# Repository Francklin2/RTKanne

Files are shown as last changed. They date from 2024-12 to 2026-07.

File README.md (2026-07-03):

# RTKanne
A Bluetooth RTK rover on a stick or box for blind people (Un rover RTK Bluetooth pour aveugles en boitier ou a fixer sur une canne)
English version below

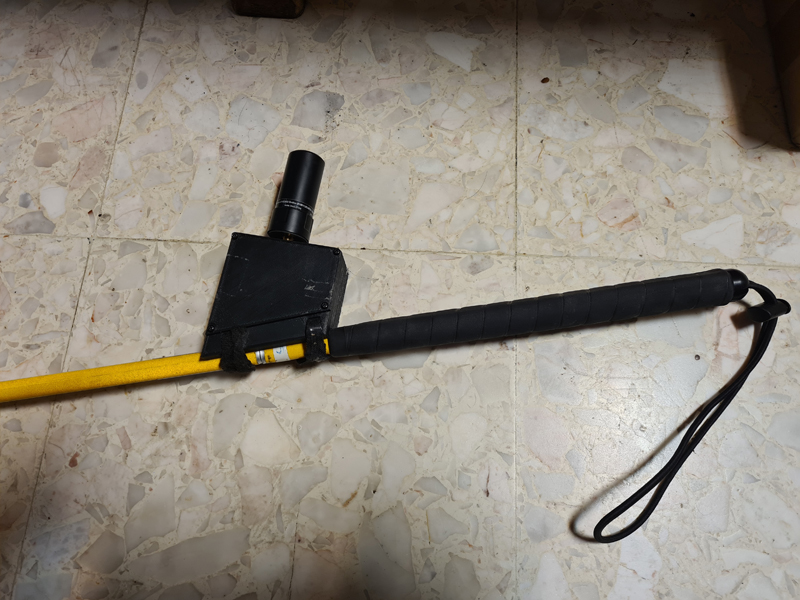
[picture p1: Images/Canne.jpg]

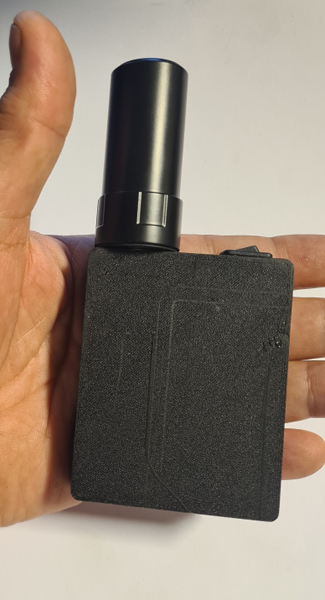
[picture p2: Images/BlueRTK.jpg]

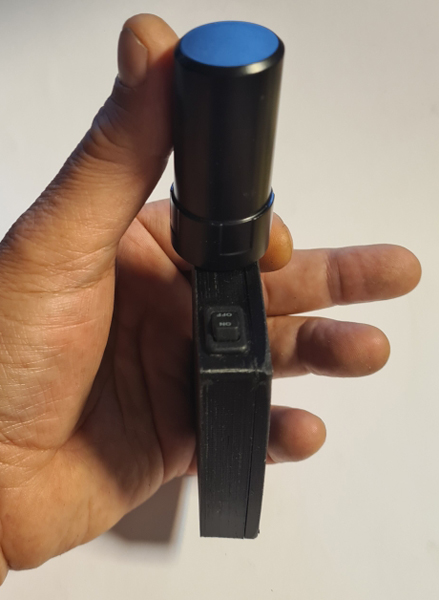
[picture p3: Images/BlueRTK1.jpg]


Les projets RTKanne et Blue RTK sont des rover RTK pour aveugles et malvoyants qui peuvent se fixer sur une canne (projet initial RTKanne) ou un boitier plus compact à mettre dans une pochette sur la poitrine avec le smartphone ou même dans une poche de ses vêtement (projet final Blue RTK),il peut fournir une précision de quelques centimètres a une application IOS ou Android. Le système est composé du ZED-X20P, un module bluetooth  ou un Bluetooth Xiao ESP32C3 (Ardusimple sur RTKANNE), une batterie interne avec son chargeur BMS USB-C et un régulateur 3,3 Volts Pololu. Un PCB de carte mère et un nouveau boitier on été développé par My Human Kit à Rennes afin de fiabiliser le boitier et simplifier sa fabrication (My Human Kit est un Fablab dédié au handicap).

Ce récepteur utilise le réseau NTRIP du réseau open source Centipede (centipede.fr) fonctionnant en France et dans certains pays d'Europe pour obtenir les corrections RTK (une connexion a internet via le smartphone est requise). 
La précision de position RTK ne permet de résoudre qu'une partie du problème de navigation et de guidage d'un aveugle, si on a bien une position précise, il faut en plus un logiciel de navigation qui soit adapté a ce niveau de précision, par exemple Google maps piéton valide un point de navigation alors que l'on est dans un rayon d'une dizaine de mètres de ce point, cette imprécision dans la carte de navigation et du trajet ne permet pas le guidage correct d'un aveugle même en RTK, il faut donc que le logiciel et le trajet de navigation soient adaptés pour tirer pleinement profit d'un positionnement précis. Pour l'instant seule l'application Sonarvision sur IOS propose des trajets précis au mètre prés  pour les aveugles et malvoyant grâce au VPS (visual positionning system) ou au récepteur RTK 

    Utilisation sur IOS
   L'application Sonarvision est disponible avec l'option RTK depuis mi 2025 avec de nouvelles fonctionnalités  afin de profiter pleinement des possibilités du RTK comme l'enregistrement de traces pour créer un parcours hors zone couvertes par le VPS ou sans passer par l'éditeur de trajets, l'application est disponible sur sonarvision.fr ou sur l'appstore. Pour tester le bon fonctionnement du Rover RTKanne, vous pouvez aussi utiliser SWmaps disponible sur l'apple store ou installer le code de Client Ntrip présent sur ce dépôt a l'aide de Xcode, il faut installer Xcode sur un Mac, charger et compiler le code de Client Ntrip, connecter l'iPhone en mode développeur au Mac pour créer cette application. Les paramètres Ntrip de centipede sont déjà configurés et on peut afficher les coordonnées de position, le nombre de satellites reçus, la précision de la position, l'état de la connexion a centipede.fr , ce code sert surtout à montrer comment le RTK peut etre ajouté à une application IOS.
   
[Video Guidage RTK avec l'application Sonarvision](https://youtu.be/zTxEzIDLCAY) 
   
      Utilisation sur Android
  Pour utiliser en rover RTKanne (Bluetooth classique Ardusimple)sur Android et que le smartphone et toutes les applications utilisent la position RTK, vous devrez installer et utiliser l'application Bluetooth GNSS qui se trouve sur le playstore. Pour que Bluetooth GNSS puisse remplacer la position donnée par le récepteur GPS du smartphone par celle donnée par le rover (fonction appelée "Mock Location") vous devrez  passer Android en mode développeur. Une fois Bluetooth GNSS paramètré avec la connexion bluetooth, la connexion au serveur Ntrip centipede.fr et le choix de la station (ou Moutpoint) la plus proche choisi (il y a une fonction pour choisir la plus proche automatiquement), vous lancez la connexion avec le bouton en bas a droite et la position RTK sera utilisée par toutes les applications qui seront lancées ensuite, mais il faut garder bluetooth GNSS en fond de tache. Ie Bluetooth BLE est en cours de développement sur Bluetooth GNSSce qui permettra d'utiliserBlie RTK,SWmaps est aussi disponible sur Android avec le BLE et dispose de l'option Mock location.

Pour ce projet, j'ai testé différents types de récepteurs GNSS pour trouver ceux qui fonctionnent bien pour cette utilisation, souvent dans des situations difficiles comme les canyons urbains ou les forêts. Le Ublox ZED-X20P est celui qui est le plus performant et que je recommande dans notre utilisation d'après mes tests, suivi du ZED-F9P dont la position est un peu moins robuste en condition difficile. Voici les récepteurs que j'ai pu tester sur le terrain:
 - Ublox ZED-X20P: récepteur triple fréquence L1 L2 L5, celui qui a une position RTK Fix la plus robuste et la plus rapide, il inclus la constellation Glonass il est compatible Galileo HAS depuis la mise à jour du firmware en version 2.10.
- Ublox ZED-F9P: Bonnes performances, pour une utilisation compatible avec le réseau Centipede, il vaut mieux choisir la version L1/L2 plutôt que L1/L5 comme le réseau centipede est majoritairement en L1/L2 (le L5 est plus robuste en ville mais moins répandu pour l'instant), il est aussi performant que le X20P en terrain découvert et peut être utilisé comme station de correction Ntrip si on en a pas a proximité. 
- les récepteurs avec IMU (centrale inertielle gyroscope/accéléromètre)comme le Ublox ZED-F9R ou le Navspark PX1175DR ne sont pas utilisables sur un piéton car il faut une installation fixe sur un châssis, on ne peut pas encore tirer parti de cette option en cas de perte de signal GNSS (tunnels etc)
- Navspark PX1122R: récepteur L1 L2, moins cher mais aussi peu moins sensible que les Ublox. Le prix de 50$ est attractif mais le port a 94$ est excessif, pas de port USB ce qui oblige a ressouder le câblage pour le configurer, le positionnement est correct.
- Bynav M10: je ne suis pas arrivé a l'utiliser car il fonctionne en 5 volts et le logiciel de configuration en ligne de commande limite utilisable et peu complet niveau options.
  Je n'ai pas testé les Unicom UM980 ni les Mosaic X5
   
   [Video COMPARE THE UBLOX ZED-F9P VS ZED-X20P](https://www.youtube.com/watch?v=RUgDCJcdhyc)
   
Le module Seeed studio Xiao ESP32C3 avec Bluetooth est une bonne alternative au Bluetooth BT+BLE Ardusimple si on n'utilise que IOS (ne ne se connecte pas encore a Bluetooth GNSS sur Android) il ne coute que 7 euros environ et fonctionne très bien. Il u a 2 versions du code: XIAO ESP32C3-BLE est optimisée pour les récepteurs Navspark tandis que la version XIAO ESP32C3-V2 est optimisée pour les récepteurs Ublox. 

L'antenne Beitian BT-560 est aussi une alternative moins couteuse à 34 euros, elle est de forme identique a celle de chez Ardusimple et offre des performances similaires. 

Voici la liste des pièces des différents projets, dans le GNSS store on a le choix pour le ZED-F9P entre les fréquences L1/L2 et L1/L5, le L1/L5 est censé être plus robuste en milieu urbain ou foret mais pour une meilleure compatibilité avec le réseau Centipede le L1 L2 est recommandé sauf si vous avez une station L1 L5 près de chez vous. On peut aussi choisir le ZED-X20P qui est en triple fréquence L1 L2 L5, il est un peu plus cher mais offre une meilleure qualité de réception en milieu perturbé et plus de précision en mode DGPS/HAS si il y a une coupure de réseau NTRIP (zone blanches GSM)  

Composants du rover Blue RTK (Boitier plus petit pour poche ou pochette ventrale) Compter 374 euros environ + 1 ilpression 3D du boitier (entre 30 et 40 euros chez un imprimeur en ligne) 

- Récepteur RTK L1/L2/L5 Ublox ZED-X20P de chez [GNSS Store](https://gnss.store/high-precision-rtk-gnss-modules/415-elt0421.html)  229,99 Euros HT/ 282 Euros TTC avec port
- Antenne L1 L2 L5 Beitian BT 560 performances similaires a la Ublox 34 Euros chez [Aliexpress](https://fr.aliexpress.com/item/32991527632.html?pdp_npi=4%40dis%21EUR%21€%2016%2C69%21€%2015%2C69%21%21%2119.00%2117.86%21%40211b876717565823921947665ef2ad%2112000031416205032%21sh%21FR%210%21X&spm=a2g0o.store_pc_allItems_or_groupList.new_all_items_2007550542376.32991527632&gatewayAdapt=glo2fra) ATTENTION il faut bien choisir la BT560 dans le shop
- Module bluetooth Seeed Studio Xiao ESP32C3 7 Euros chez [Aliexpress](https://fr.aliexpress.com/item/1005007039705247.html?pdp_npi=4%40dis%21EUR%21€%200%2C16%21€%200%2C15%21%21%211.26%211.26%21%402103890117565830582966233e6eec%2112000049940483727%21sh%21FR%210%21X&spm=a2g0o.store_pc_allItems_or_groupList.new_all_items_2008969535028.1005007039705247&gatewayAdapt=glo2fra)
- Batterie Lithium Huawei HB434666RBC 1S (4,2V) de 1500mAh pour une 8 heures environ d'autonomie, 18,90  euros [Les batteries du web](https://www.lesbatteriesduweb.fr/batterie-telephone-portable-pour-huawei-hb434666rbc-xml-5799_10491-1063348.html)
- Régulateur 3,3V Pololu S9V11F3S5C3 avec coupure d'alimentation a 3V afin de préserver la batterie d'une décharge excessive.( https://www.pololu.com/product/2873 ) 10,85 $
- BMS 1S 1A USB-C TP4056 pour la recharge de la batterie interne ( https://www.otronic.nl/fr/chargeur-de-batterie-lithium-18650-avec-usb-c-5v-1.html ) 1,49 Euros
- Interrupteur ON/OFF (https://www.ebay.fr/itm/251390016446) ou (https://www.aliexpress.com/item/1005001792406484.html) 
- Boitier imprimé 3D Blue RTK (version avec et sans PCB)
Pour elle montage des composants avec un PCB acheter en plus:
- PCB pour la version avec carte mère (plus simple à monter et plus fiable) 20,40 euros chez [Aisler](https://aisler.net/p/GPDCRTQV)
- Barrette mâle droit 2,54mm sécable 40pin (https://www.ebay.fr/itm/116002953919?var=416149221180)
- Connecteur JST XH 2,54mm avec cable silicone pour la batterie et l'interrupteur 1,76 euros chez [Aliexpress](https://fr.aliexpress.com/i/1005007169294004.html?gatewayAdapt=glo2fra)
- visserie et rondelles pour le boitier, Philips m2x10mm tête fraisée + M2x5mm tête plate, rondelle plastique.

Composants du rover RTKanne compter environ 448 euros + 1 impression 3D (30/40 euros chez un imprimeur en ligne)

- Récepteur RTK L1/L2 Ublox ZED-F9P ou ZED-X20P https://gnss.store/zed-f9p-gnss-modules/273-200-elt0412.html#/61-gnss_module-l1_l2_zed_f9p 189,99 Euros HT
- Antenne L1 L2 L5 pour drones afin d'avoir une antenne de petite taille avec une bonne qualité de réception ( https://gnss.store/gnss-rtk-multiband-antennas/28-elt0014.html ) 69 Euros
- Module bluetooth  BT+BLE bridge Ardusimple, compatible Android et IOS ( https://fr.ardusimple.com/product/ble-bridge/ ) 66 Euros
- Batterie Lithium polymère 1S (4,2V) de 1500mAh pour une dizaine d'heures d'autonomie, une batterie de plus grande capacité est possible.[Les batteries du web](https://www.lesbatteriesduweb.fr/batterie-telephone-portable-pour-huawei-hb434666rbc-xml-5799_10491-1063348.html)
- Régulateur 3,3V Pololu S9V11F3S5C3 avec coupure d'alimentation a 3V afin de préserver la batterie d'une décharge excessive.( https://www.pololu.com/product/2873 ) 10,90 euros
- BMS 1S 1A USB-C TP4056 pour la recharge de la batterie interne ( https://www.otronic.nl/fr/chargeur-de-batterie-lithium-18650-avec-usb-c-5v-1.html ) 1,49 Euros
- Interrupteur ON/OFF ( https://www.ebay.fr/itm/251390016446 )
- Boitier imprimé 3D RTKanne pouvant se fixer sur une canne 

Ardusimple propose ussi des Kits RTK, comme ils sont dépourvu de batterie interne ils néccessitent un powerbank et sont plus encombrants mais plus simples a assembler (pas de soudure)
Composants du kit rover RTK2B Ardusimple (voir aussi sur leur site,le RTK3B basé sur le ZED-X20P)
 
 - Récepteur RTK L1/L2 Ublox ZED-F9P https://fr.ardusimple.com/product/simplertk2b/ 193 Euros
 - Module bluetooth  BT+BLE bridge Ardusimple, compatible Android et IOS  https://fr.ardusimple.com/product/ble-bridge/ 66 Euros
 - Boitier imprimé 3D https://fr.ardusimple.com/product/plastic-case-simplertk2b/ 49 Euros
 - Antenne multi fréquences pour drones afin d'avoir une antenne de petite taille avec une bonne qualité de réception https://fr.ardusimple.com/product/helical-antenna/ 99 Euros
 -  Manuel BT+BLE bridge pour le connecter au ZED-F9 https://fr.ardusimple.com/btble-bridge-hookup-guide/

   Kit Ardusimple RTK Handheld Surveyor, composants similaires au RTK2B mais livré en lot ce qui est moins cher que le kit RTK2B (livré non monté) Je n'ai pas monté ce kit mais on devrait pouvoir l'utiliser sans la poignée ou le support smartphone si l'on veut, on peut aussi utiliser un powerbank USB-C pour l'alimenter et économiser la batterie du téléphone.
   - https://fr.ardusimple.com/product/rtk-handheld-surveyor-kit/  399 euros
   - Manuel d'assemblage et mise en route avec SWmaps https://fr.ardusimple.com/user-manual-handheld-surveyor-kit/
   - Manuel de configuration U-center https://fr.ardusimple.com/how-to-configure-ublox-zed-f9p/

  Le positionnement RTK (real time kinematic) est un système qui utilise un récepteur mobile (le rover) et des stations (les bases, stations ou moutpoint) qui lui apportent les corrections de position nécessaire pour obtenir une précision pouvant aller jusqu'au centimètre. Pour obtenir une bonne précision il faut etre a moins de 40Km d'une base mais pour notre utilisation on peut aller jusqu'a 70Km, il faut donc une couverture complète du pays avec des stations de corrections et l'accès a ces services est payant par abonnement, depuis quelques années un réseau de stations open source et gratuit s'est développé grâce au agriculteurs: le réseau [centipede](https://docs.centipede.fr) , ce réseau permet de se connecter au stations via un client Ntrip, si il n'y a pas de station dans la région, on peut en construire une avec un faible cout (envirton 400 euros) et l'ajouter au réseau, ce qui a permit au réseau centipede de s'agrandir rapidement. Vous pourrez trouver toutes les informations pour construire et connecter sa base ou son rover sur [centipede.fr](https://docs.centipede.fr) . Le réseau centipede est composé a environ 90% de stations au fréquences L1/L2, il est donc préférable de choisir un récepteur RTK en L1/L2 plutôt que la version L1/L5, le ZED-X20P triple bande L1/L2/L5 un peu plus couteuse (229 euros HT contre 189 euros HT) mais a la qualité de réception et une précision plus robuste  

	Schéma de connexion ZED-X20P/ZED-F9P
    Le récepteur est connecté au module bluetooth par les connecteurs TX et RX en croisant les entrée/sortie TX>RX et RX>TX. Les 2 modules sont alimentés par la sortie 3,3volts du régulateur Pololu, celui ci est branché sur la sortie batterie du BMS via l'interrupteur. La batterie est aussi connectée au chargeur (BMS) USB-C. La batterie est logée dans le compartiment de l'autre coté du boitier.

Vous trouverez plus d'infos sur la configuration du récepteur dans le [Wiki](https://github.com/Francklin2/RTKanne/wiki) 

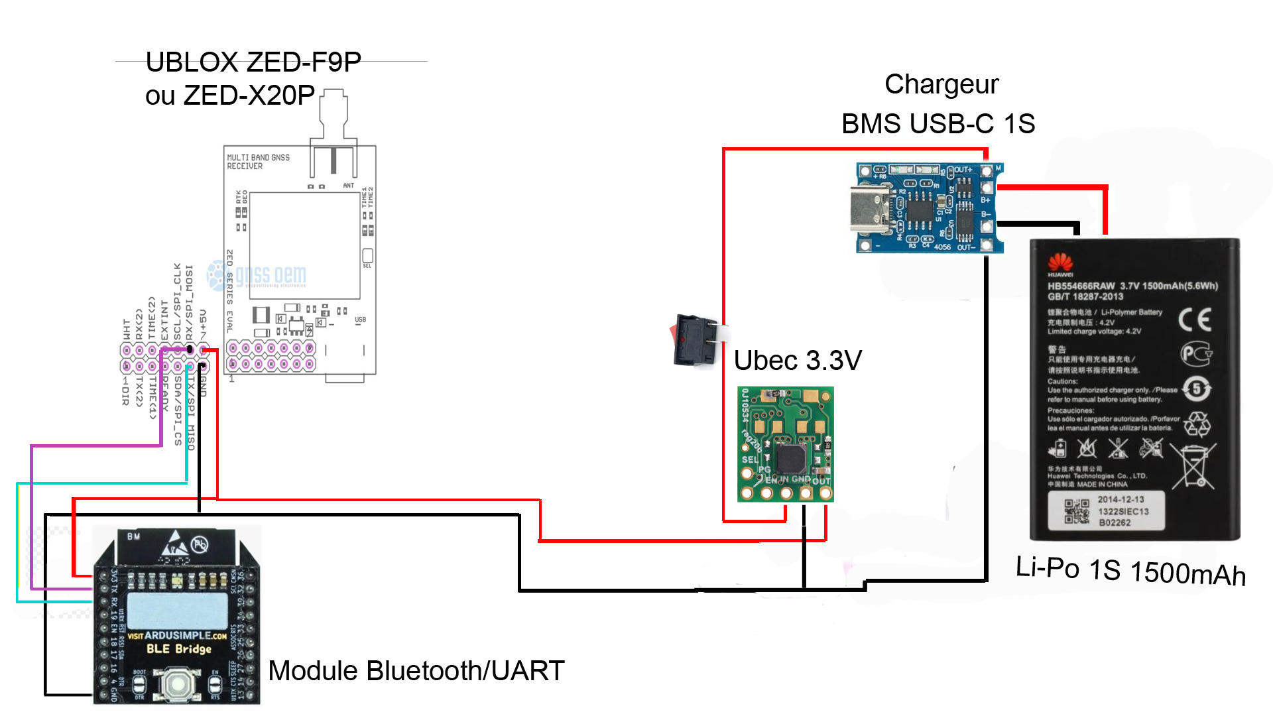
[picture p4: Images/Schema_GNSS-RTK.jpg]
    

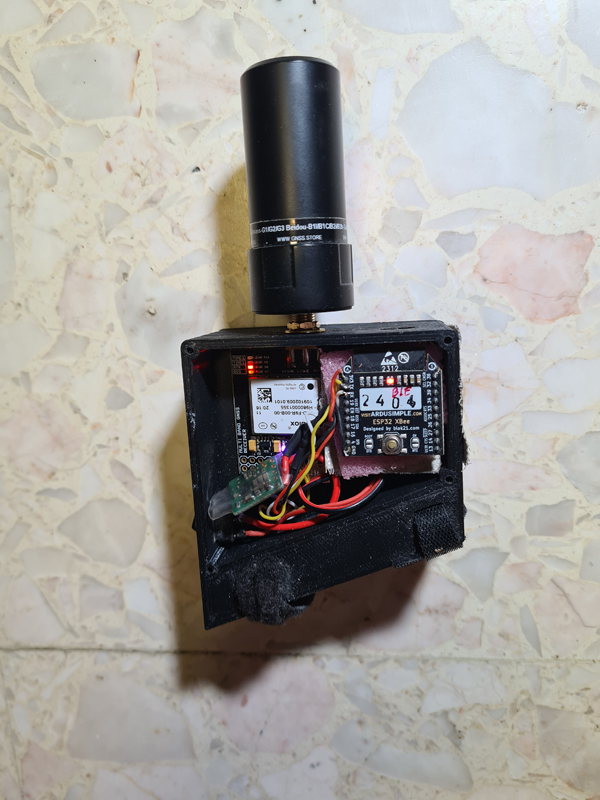
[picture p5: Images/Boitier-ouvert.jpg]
  

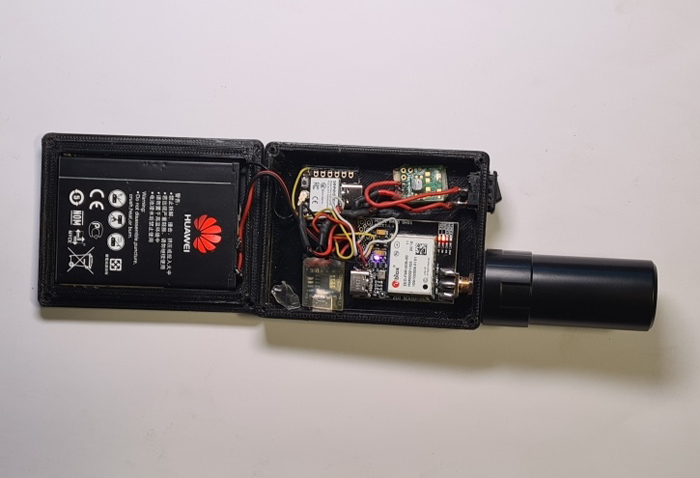
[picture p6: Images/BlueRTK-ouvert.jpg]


# RTKanne
A RTK rover on a stick for blind people

  The RTKanne project is an RTK rover for blind and visually impaired people that can be attached to a cane, providing centimeter-level accuracy to an Android or iOS application. The system consists of a Ublox ZED-F9R GNSS receiver, an Ardusimple Bluetooth module compatible with Android/iOS, an internal battery, and uses the open-source Centipede network (centipede.fr) in France and some European countries for RTK corrections (an internet connection via smartphone is required to connect to the centipede.fr server). On Android, the Bluetooth GNSS application available on the Play Store must be used for all Android applications to utilize RTK precision. On iOS, each application needs to be modified to use RTK. The Sonarvision guidance app for blind and visually impaired people will soon be available with an RTK version compatible with RTKanne. Currently, only SWmaps (which is not a guidance application) on iOS allows testing on iOS. A Ntrip client program in Swift is available here to display GPS coordinates and rover status for testing and to facilitate adaptation of other applications.
RTK position accuracy only solves part of the navigation and guidance problem for a blind person. While we have an accurate position, we also need navigation software adapted to this level of precision. For example, Google Maps pedestrian mode validates a navigation point when you are within a radius of about ten meters from that point. This imprecision in the navigation map does not allow for correct guidance of a blind person even with RTK. Therefore, the code and navigation plan must be adapted to fully benefit from accurate positioning. Currently, only the Sonarvision app on iOS has precise guidance to the nearest meter for blind and visually impaired people thanks to VPS (visual positioning system) and is in the process of adding RTK to its application.
Rover components:
 - Ublox ZED-F9R RTK receiver with inertial measurement unit, which compensates for reception losses in urban environments  ( https://gnss.store/zed-f9r-dead-reckoning-gnss-modules/134-elt0117.html )
 - Multi-frequency antenna for drones to have a small antenna with good reception quality ( https://gnss.store/gnss-rtk-multiband-antennas/28-elt0014.html )
 - Ardusimple BT+BLE bridge Bluetooth module, compatible with Android and iOS ( https://www.ardusimple.com/product/ble-bridge/ )
 - 1S (4.2V) 1500mAh Lithium Polymer battery for about ten hours of autonomy, a higher capacity battery is possible
 - Pololu S9V11F3S5C3 3.3V regulator with power cut-off at 3V to protect the battery from excessive discharge ( https://www.pololu.com/product/2873 )
 - TP4056 1S 1A USB-C BMS for internal battery charging ( https://www.otronic.nl/fr/chargeur-de-batterie-lithium-18650-avec-usb-c-5v-1.html )
 - ON/OFF switch ( https://www.ebay.fr/itm/251390016446 )
 - 3D printed case that can be attached to a cane or worn in an external pouch on the belt or arm

This project uses the Ublox ZED-F9R L1/L2 RTK GNSS receiver instead of the more common ZED-F9P because it also integrates an IMU (inertial measurement unit with gyroscope and accelerometer) to compensate for GPS signal losses in urban environments or under bridges/tunnels. Its accuracy is 2 meters of error over 100 meters during satellite signal loss while supporting movements and vibrations when attached to a cane. The receiver should be configured with the U-center software before it can be used with Bluetooth and applications.
RTK (real-time kinematic) positioning is a system that uses a mobile receiver (the rover) and stations (bases, stations, or mountpoints) that provide the necessary position corrections to achieve accuracy up to the centimeter level. For good accuracy, you need to be within 40km of a base, but for our use, we can go up to 70km. Therefore, complete country coverage with correction stations is needed, and access to these services is usually paid by subscription. In recent years, an open-source and free network of stations has been developed thanks to farmers: the centipede network. This network allows connection to stations via an Ntrip client. If there is no station in the region, one can be built at a low cost and added to the network, which has allowed the centipede network to expand rapidly. You can find all the information to build and connect your base or rover on centipede.fr.

Using on Android:
To use RTKanne as a rover on Android and have the smartphone and all applications use the RTK position, you will need to install and use the Bluetooth GNSS application from the Play Store. For Bluetooth GNSS to replace the position given by the smartphone's GPS receiver with that given by the rover (a function called "Mock Location"), you will need to put Android in developer mode. Once Bluetooth GNSS is set up with the Bluetooth connection, the connection to the centipede.fr Ntrip server, and the choice of the nearest station (or Mountpoint) selected (there is a function to choose the nearest automatically), you start the connection with the button at the bottom right, and the RTK position will be used by all applications launched afterwards, but you need to keep Bluetooth GNSS running in the background.

Using on iOS:
The Sonarvision application is currently in beta testing and should be available with the RTK option in april 2025. To test the proper functioning of the RTKanne Rover, you can use SWmaps available on the App Store or install the Ntrip Client code present in this repository using Xcode. You need to install Xcode on a Mac, load and compile the Ntrip Client code, connect the iPhone in developer mode to the Mac to create this application. The Ntrip parameters for centipede are already configured, and you can display position coordinates, the number of satellites received, position accuracy, and the connection status to centipede.fr.

Connection diagram:

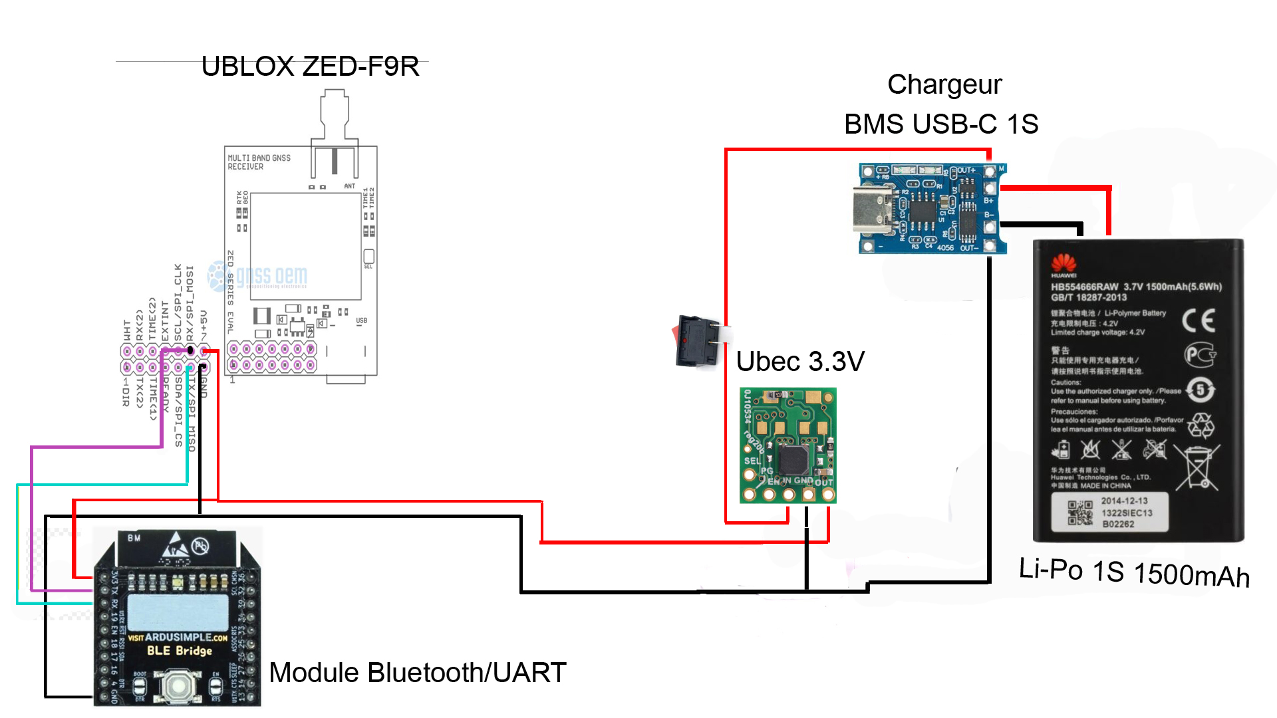
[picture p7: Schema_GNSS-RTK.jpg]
  

The receiver is connected to the Bluetooth module via the TX and RX connectors, crossing the input/output TX>RX and RX>TX. Both modules are powered by the 3.3-volt output of the Pololu regulator, which is connected to the battery output of the BMS via the switch. The battery is also connected to the USB-C charger (BMS). The battery is housed in the compartment on the other side of the case.

You can find more information on receiver configuration in the [Wiki](https://github.com/Francklin2/RTKanne/wiki)

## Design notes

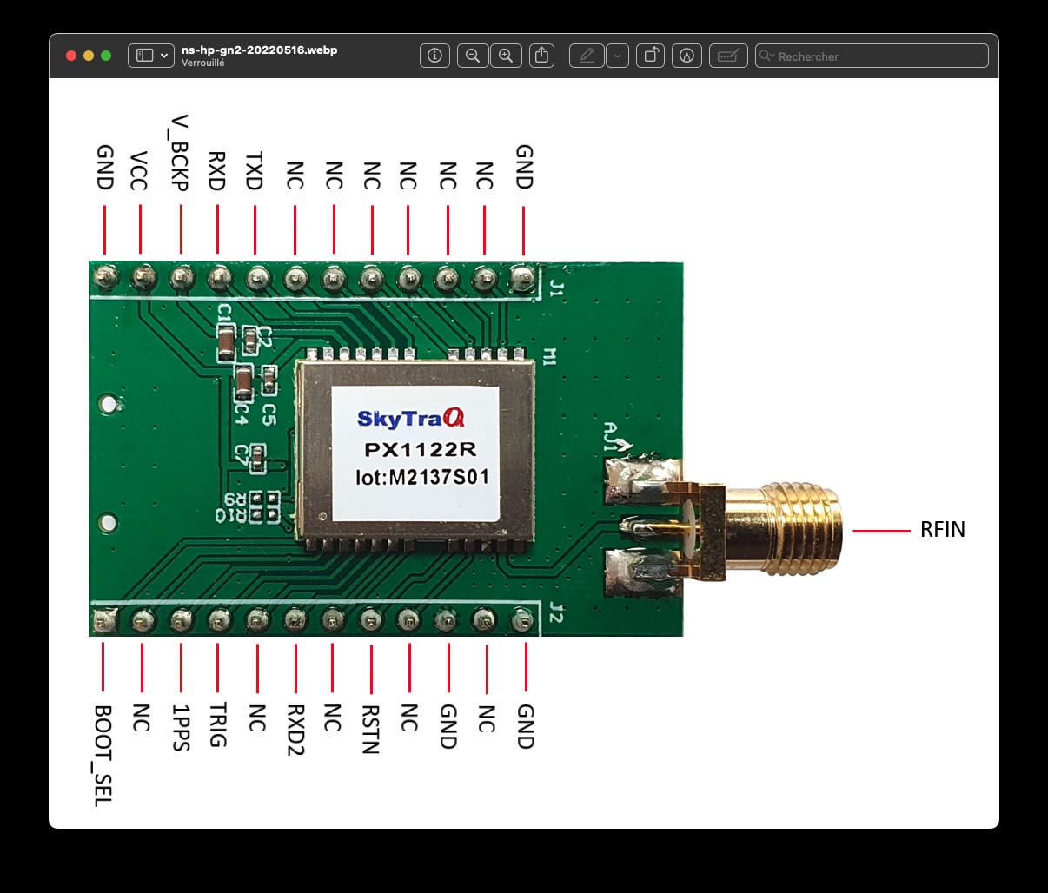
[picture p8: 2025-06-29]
Images/PX1122R-pinout.jpg

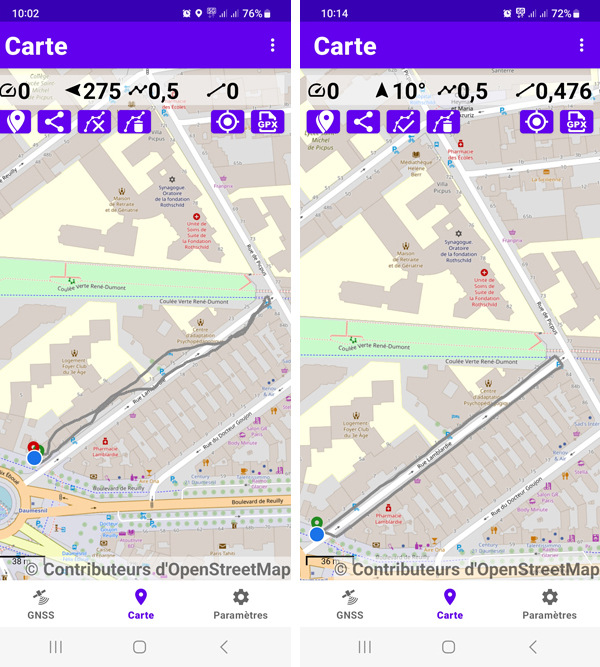
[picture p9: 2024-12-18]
Images/Comparatif.jpg

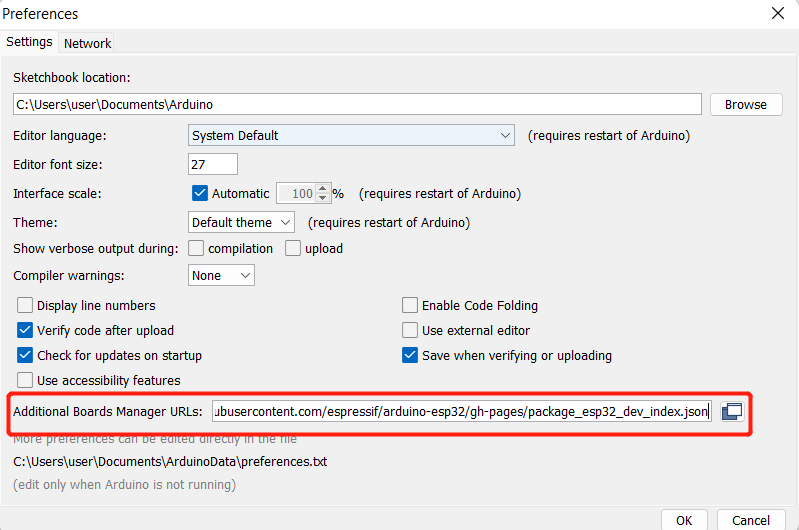
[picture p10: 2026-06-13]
Images/add_board.png

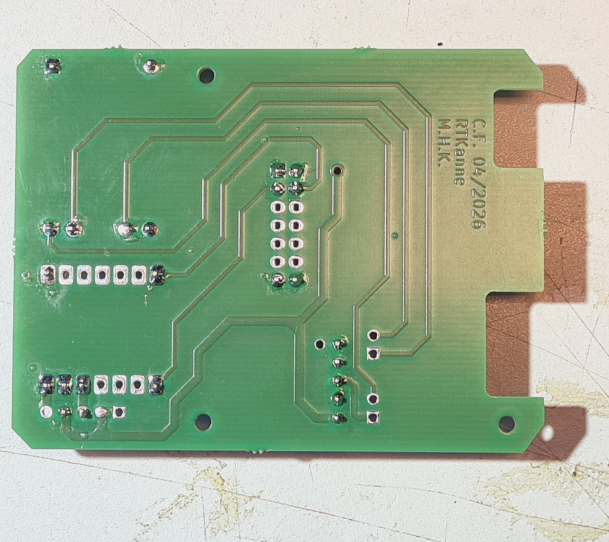
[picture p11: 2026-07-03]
Images/PCB-Soudé-dessous.jpg

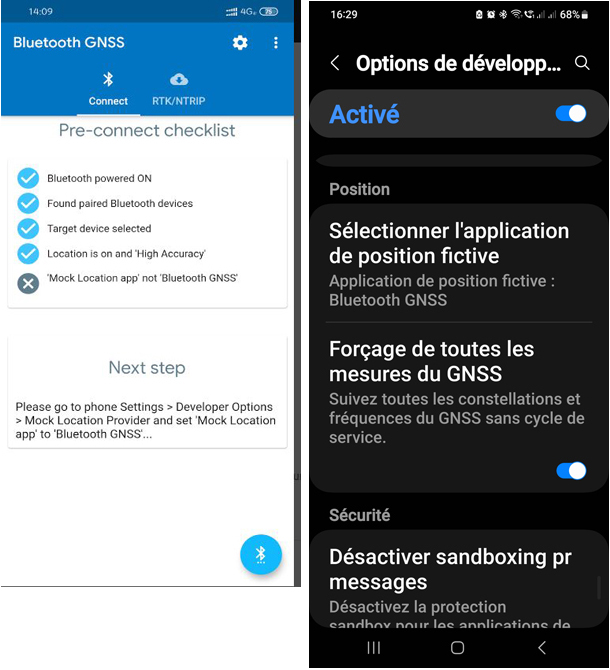
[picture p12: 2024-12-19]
Images/MockLocation.jpg

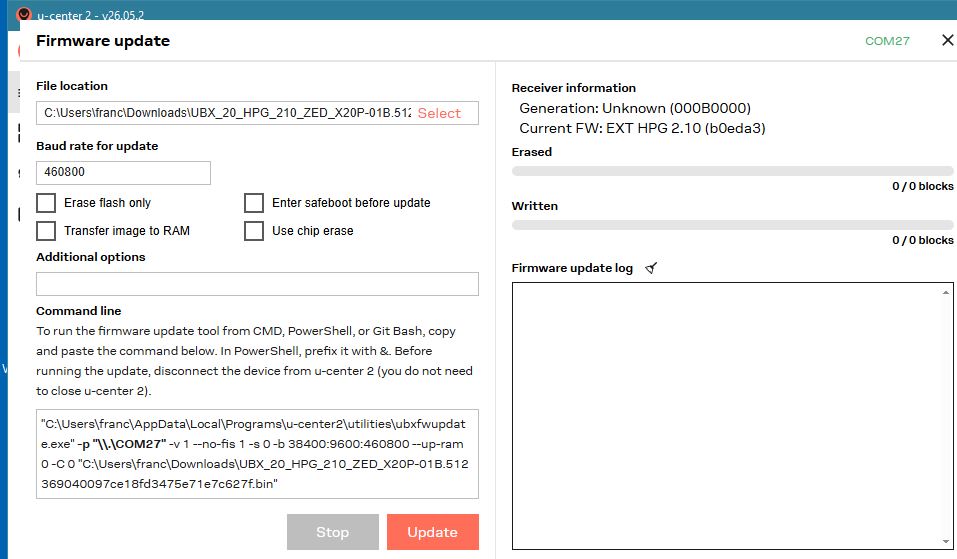
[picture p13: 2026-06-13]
Images/X20P-Update-Firmware.JPG

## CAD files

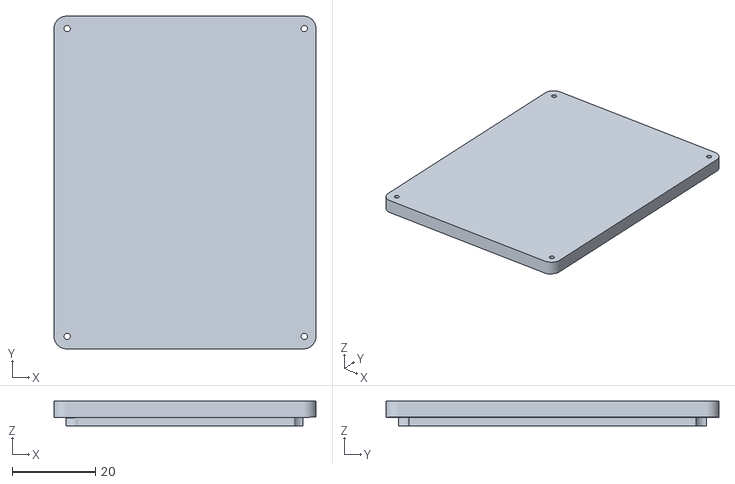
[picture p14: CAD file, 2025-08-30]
3D-print/Boitier-BlueRTK/Version-avec-cablage-interne/Capot-slim-V9.stl
63.0 x 80.0 x 6.00

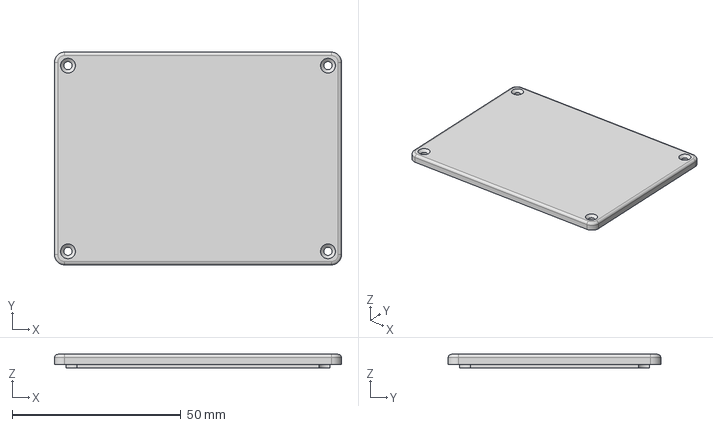
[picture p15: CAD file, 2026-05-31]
3D-print/Boitier-BlueRTK/Version-avec-PCB/Boitier_RTK - Haut.step
85.0 x 63.0 x 4.00 mm

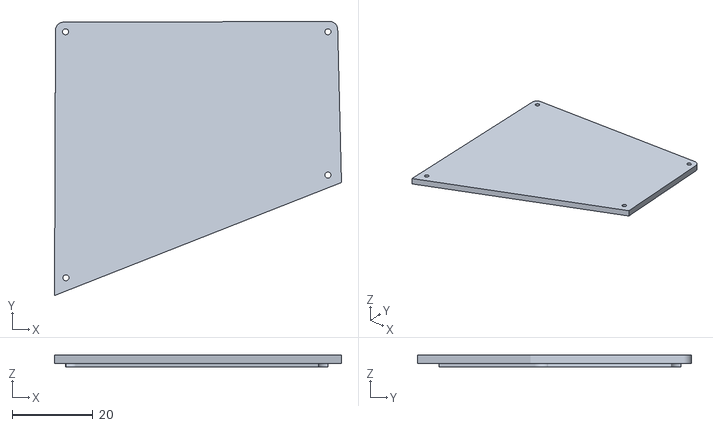
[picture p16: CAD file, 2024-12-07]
3D-print/Boitier-RTKanne/Capot gnss RTK 15D.stl
71.1 x 67.9 x 3.02

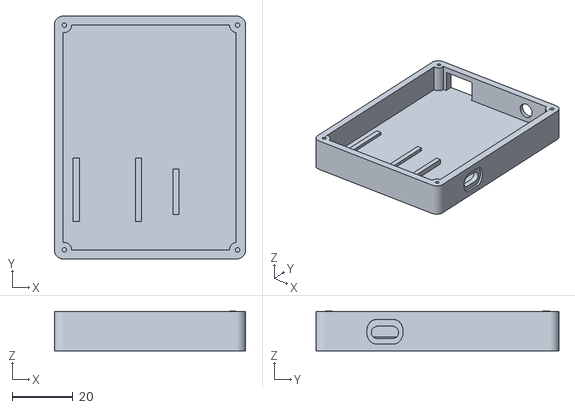
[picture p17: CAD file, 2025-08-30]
3D-print/Boitier-BlueRTK/Version-avec-cablage-interne/Boitier-slim-V9.stl
63.0 x 80.0 x 13.0

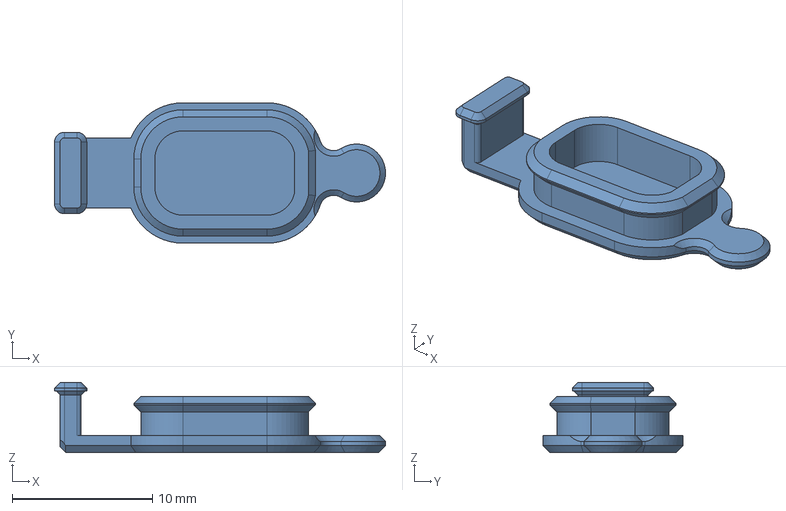
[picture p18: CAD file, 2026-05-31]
3D-print/Boitier-BlueRTK/Version-avec-PCB/Bouchon.step
23.6 x 10.0 x 5.00 mm

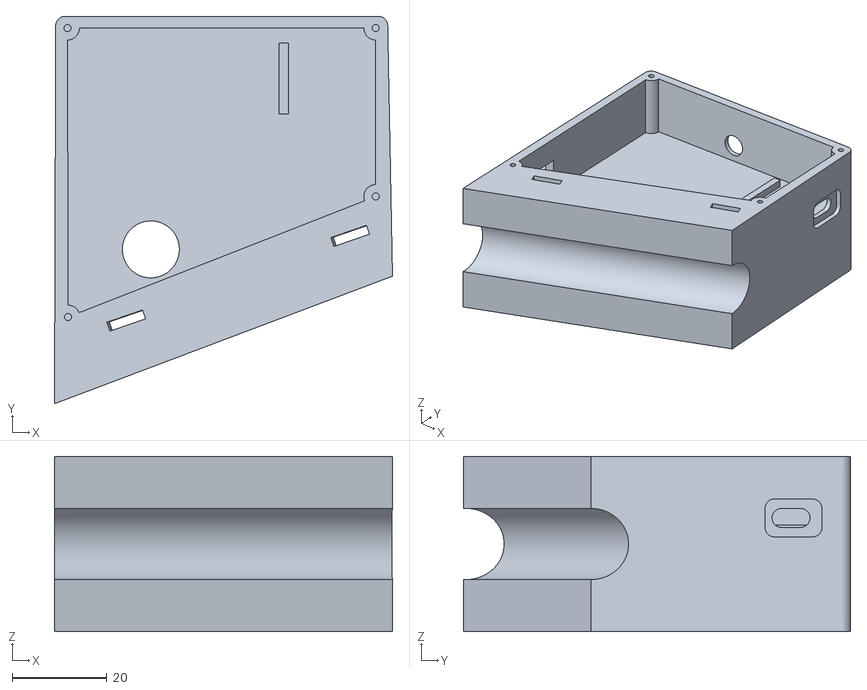
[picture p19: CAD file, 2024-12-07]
3D-print/Boitier-RTKanne/Boitier gnss RTK 16.stl
71.3 x 81.7 x 37.0

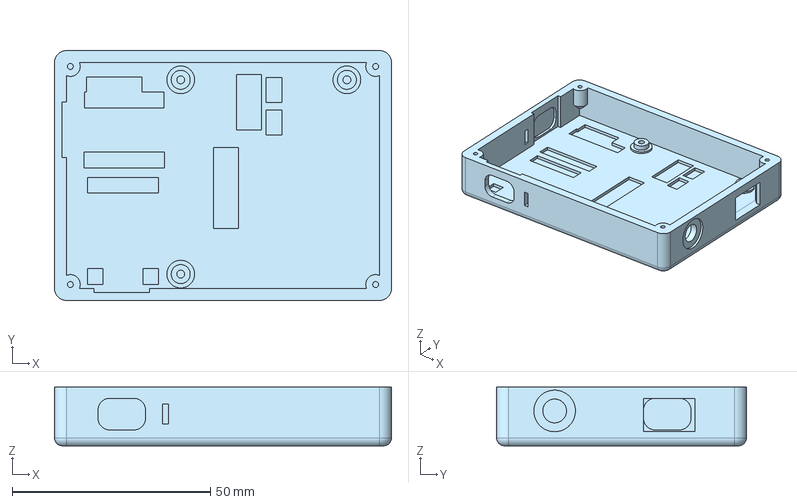
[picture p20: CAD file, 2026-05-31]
3D-print/Boitier-BlueRTK/Version-avec-PCB/Boitier_RTK - Fond.step
85.0 x 63.0 x 14.8 mm

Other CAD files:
3D-print/Boitier-RTKanne/Capot gnss RTK 15G.stl
3D-print/Boitier-BlueRTK/Version-avec-PCB/Boitier_RTK - Fond.stl
3D-print/Boitier-BlueRTK/Version-avec-PCB/Boitier_RTK - Haut.stl
3D-print/Boitier-BlueRTK/Version-avec-PCB/Bouchon.stl

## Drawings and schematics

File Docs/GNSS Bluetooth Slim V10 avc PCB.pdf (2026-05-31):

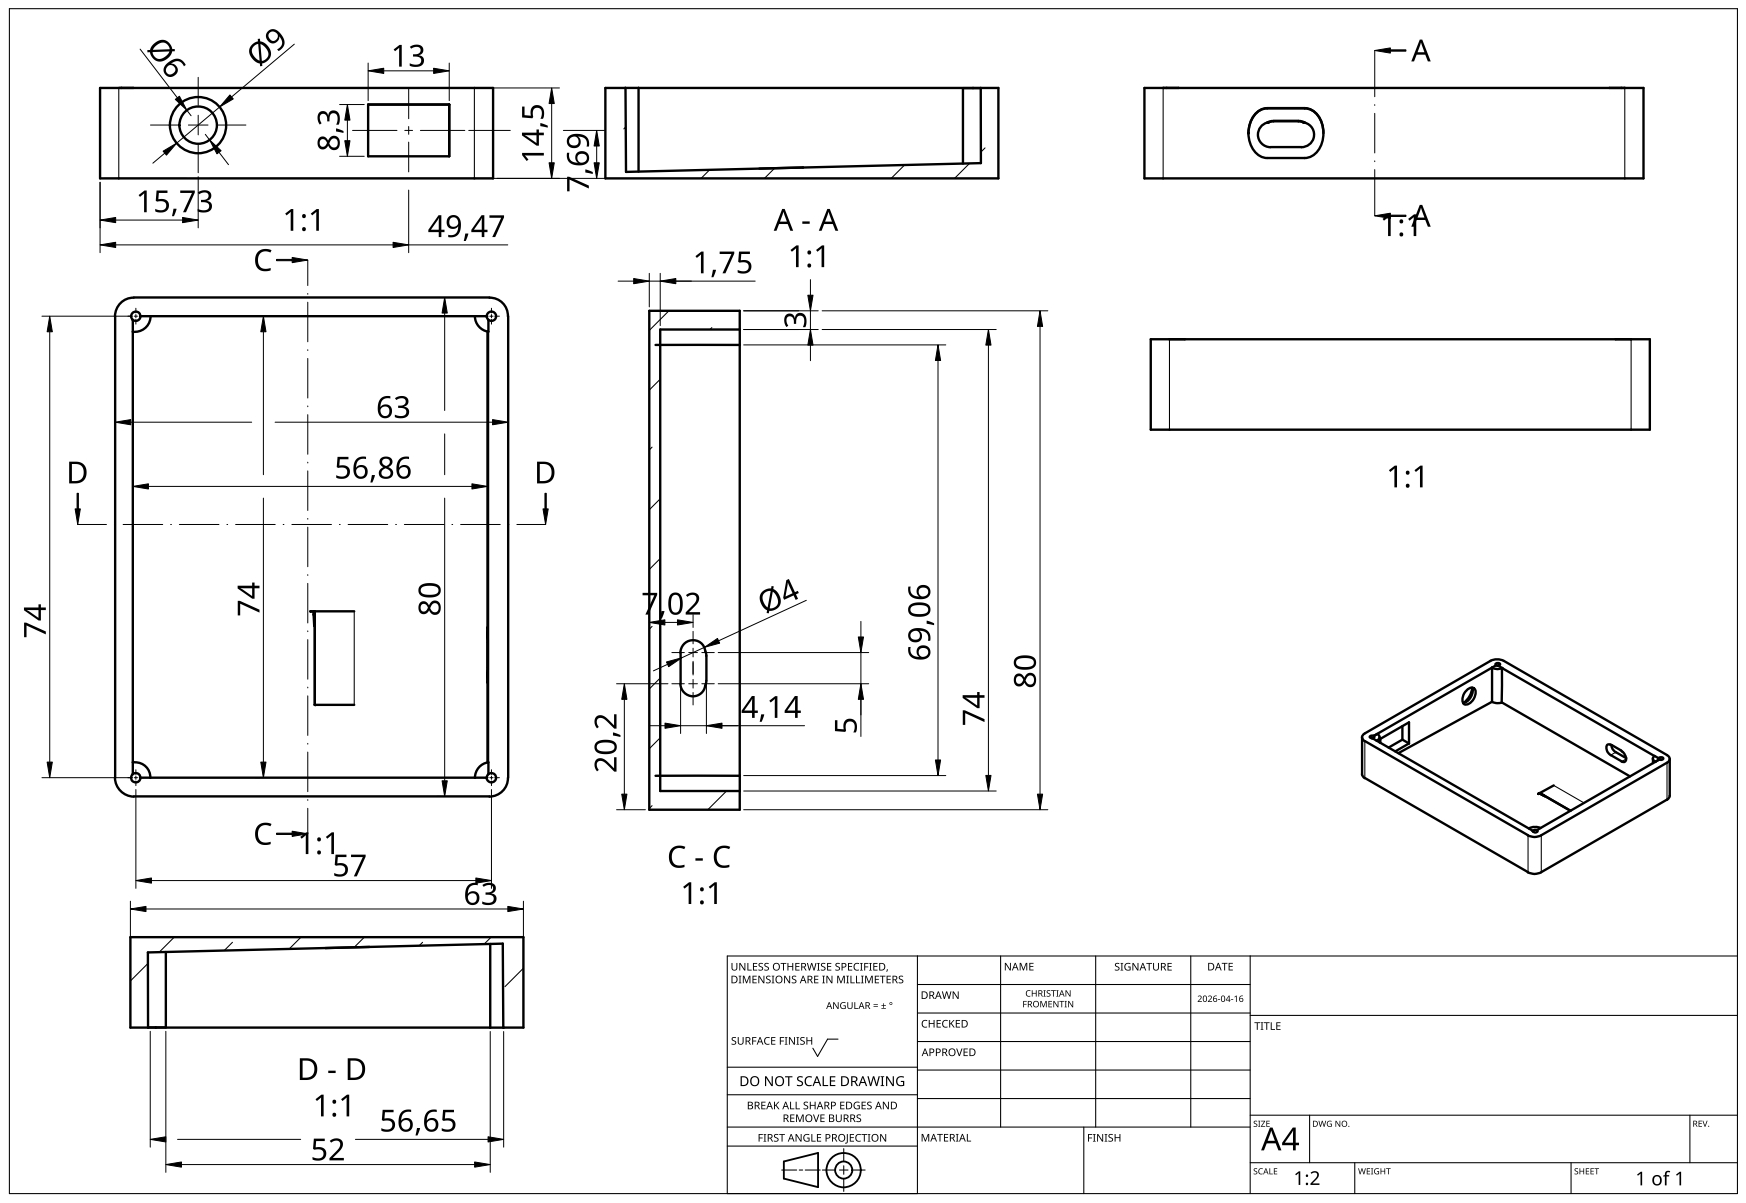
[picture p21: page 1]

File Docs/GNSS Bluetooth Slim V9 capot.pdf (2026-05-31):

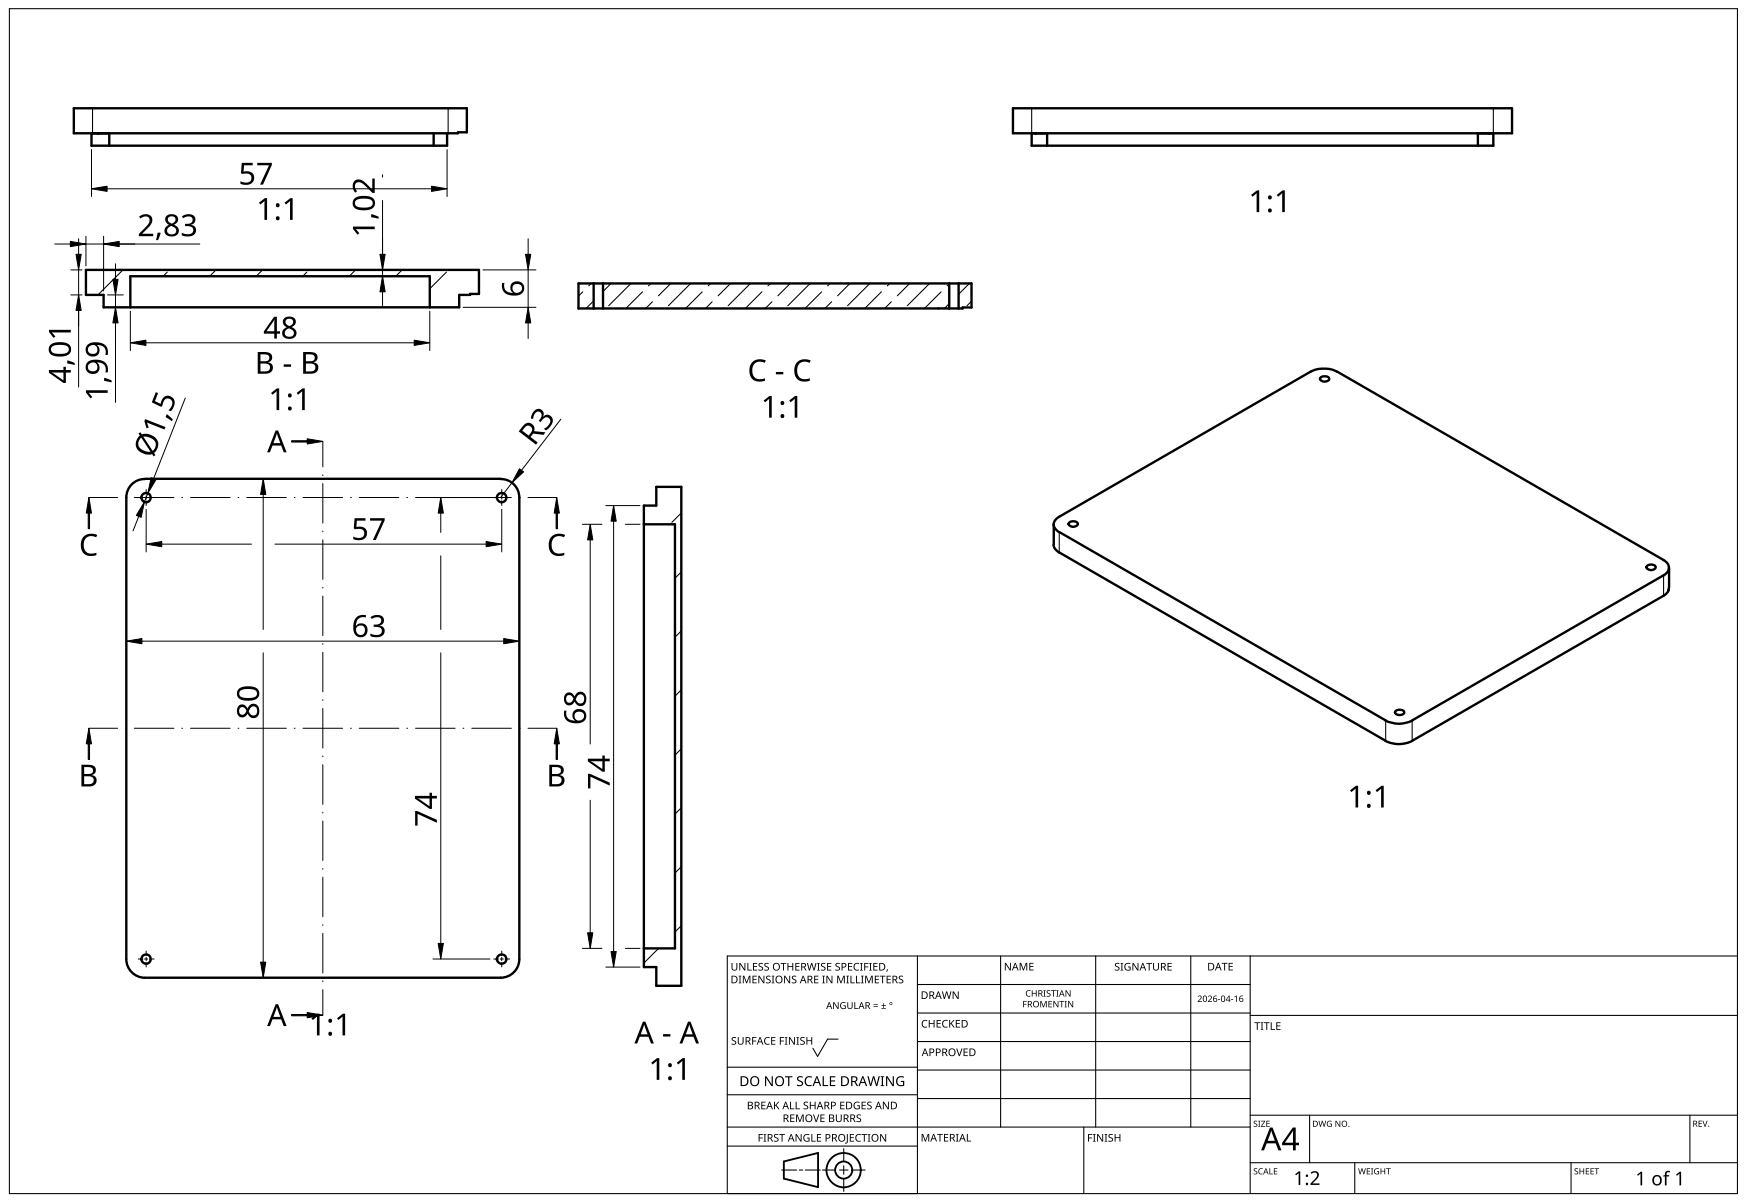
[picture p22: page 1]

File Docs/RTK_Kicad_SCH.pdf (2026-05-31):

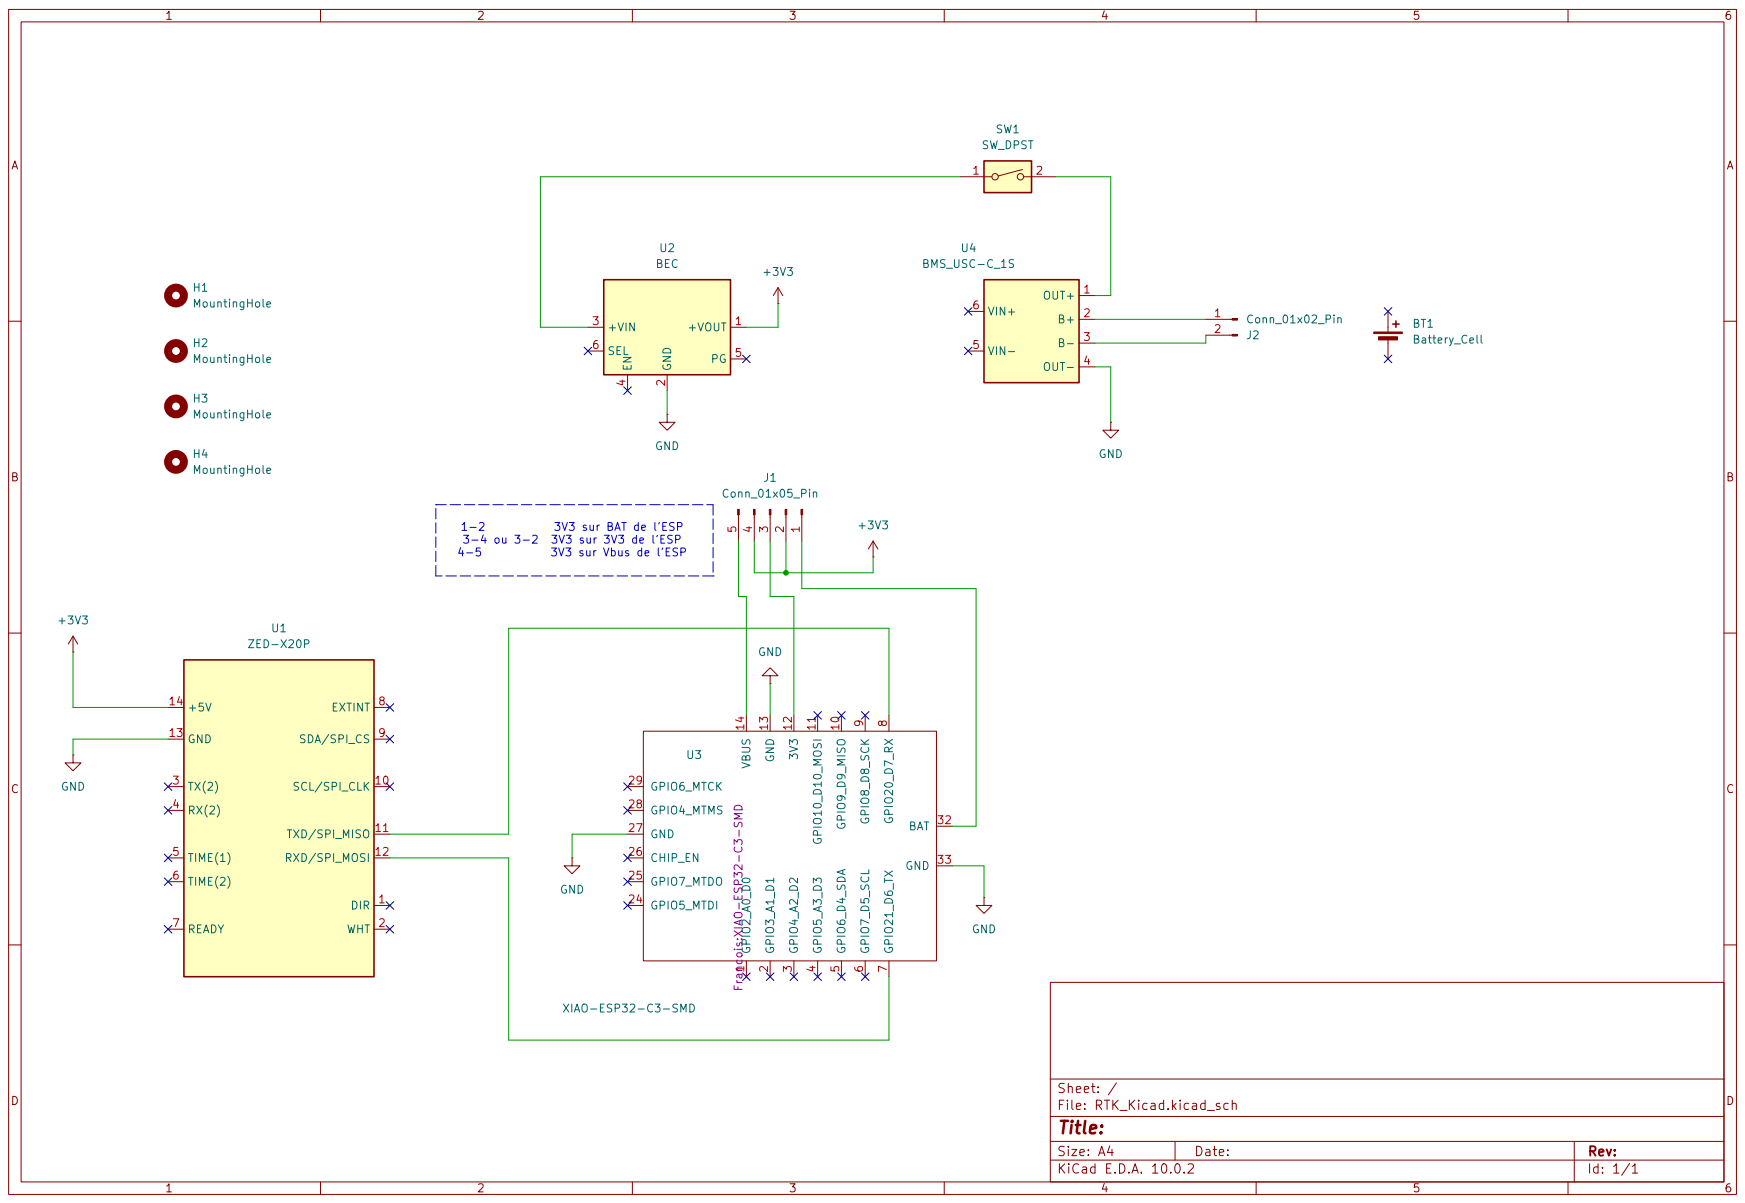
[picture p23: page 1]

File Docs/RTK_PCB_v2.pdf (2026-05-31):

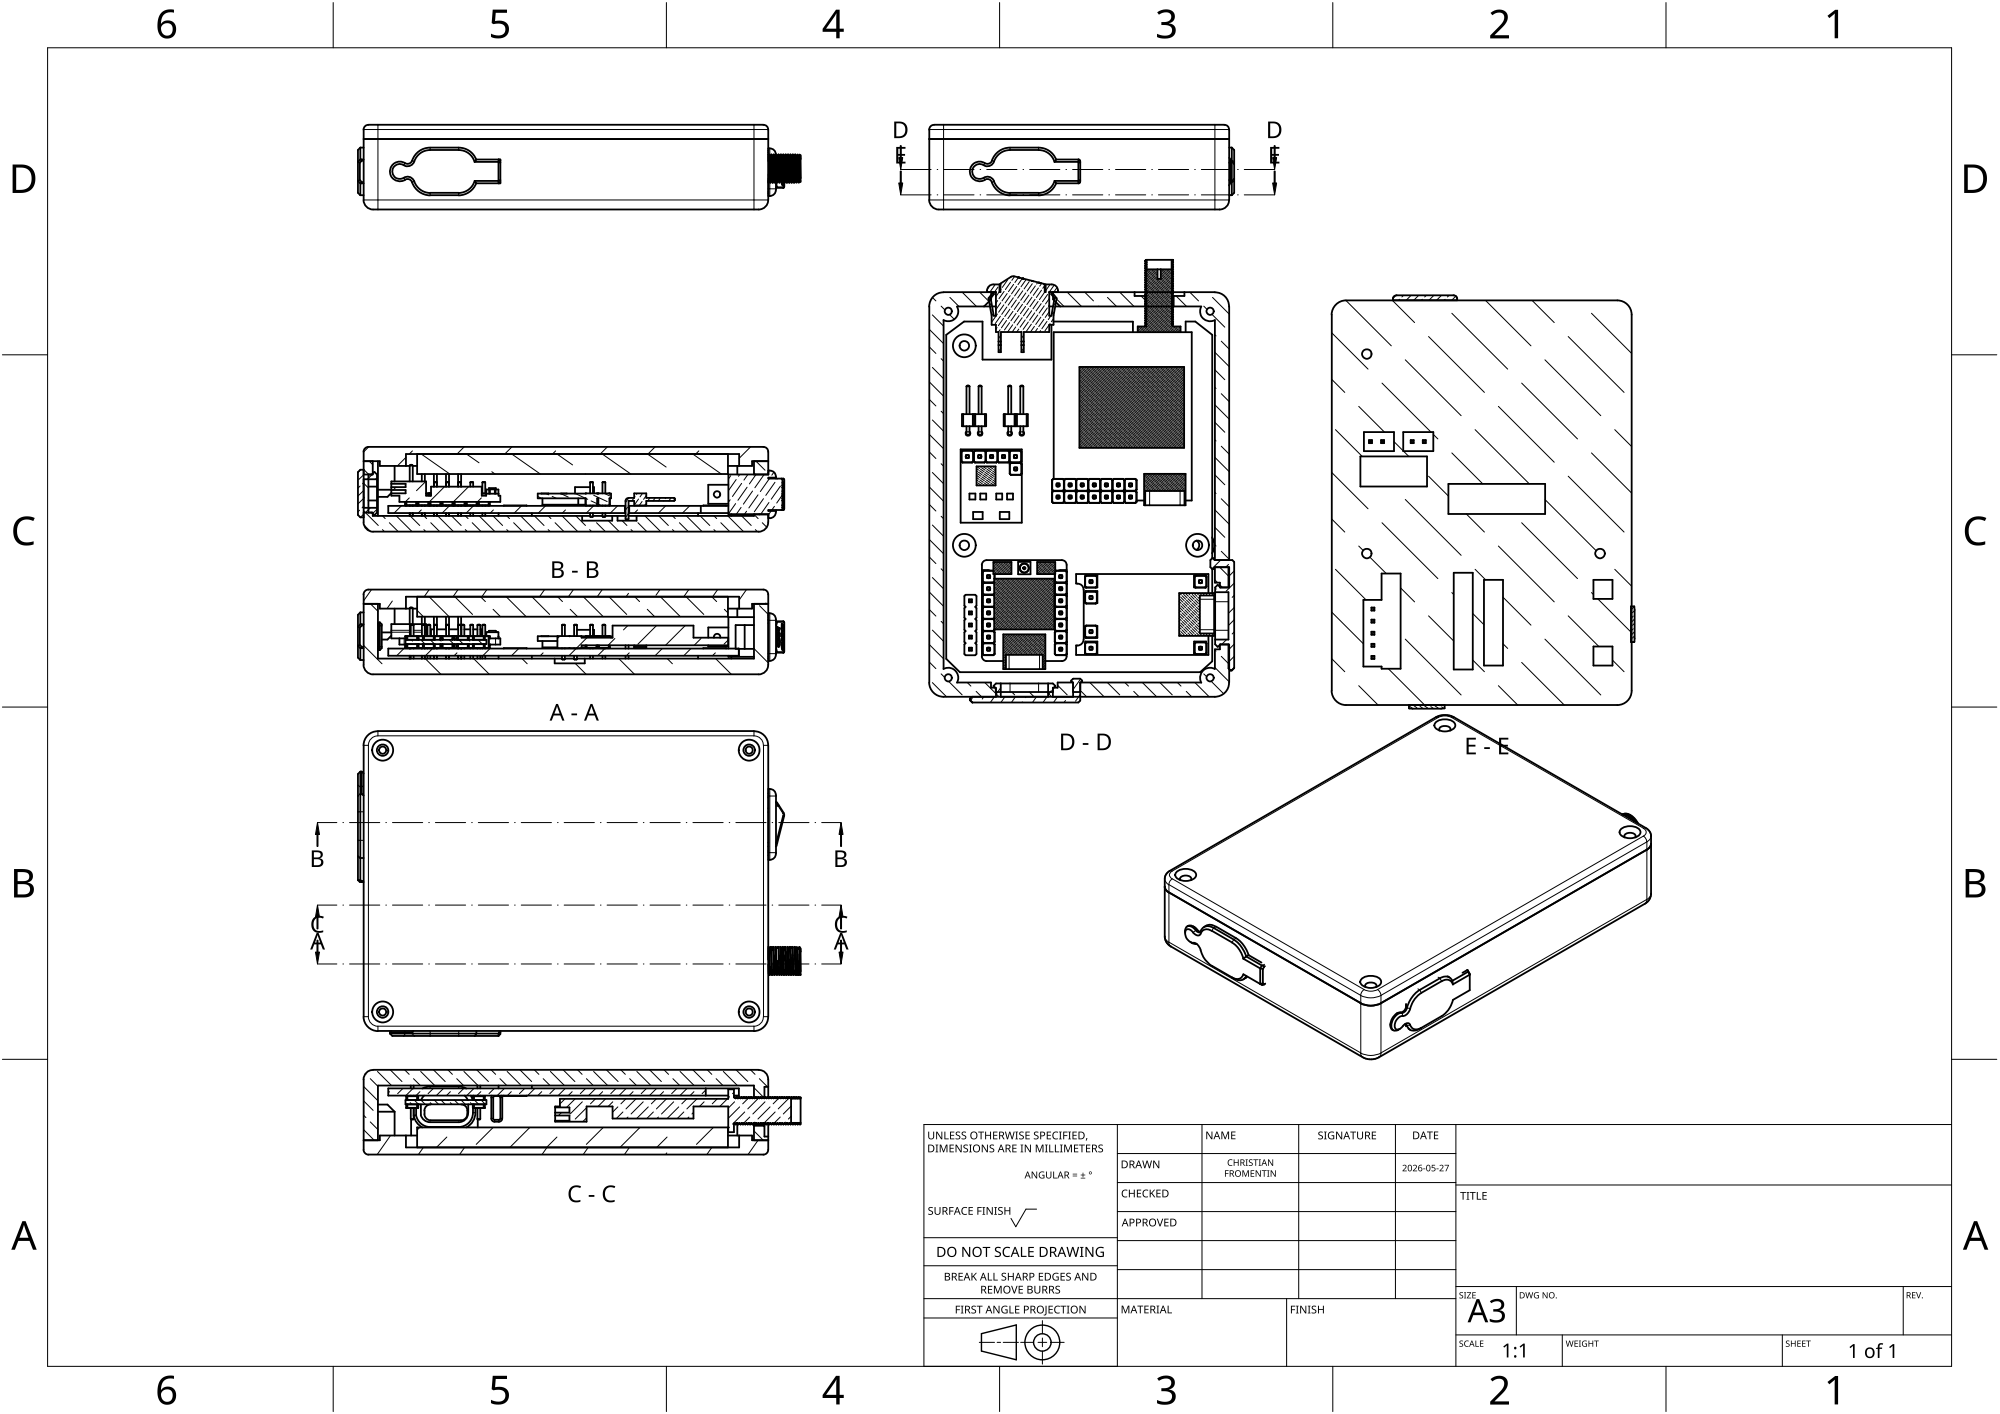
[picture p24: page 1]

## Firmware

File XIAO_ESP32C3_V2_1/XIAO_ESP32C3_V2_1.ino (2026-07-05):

#include <BLEDevice.h>
#include <BLEServer.h>
#include <BLEUtils.h>
#include <BLE2902.h>

// Nordic UART Service UUID definitions
#define SERVICE_UUID           "6E400001-B5A3-F393-E0A9-E50E24DCCA9E"
#define CHARACTERISTIC_UUID_RX "6E400002-B5A3-F393-E0A9-E50E24DCCA9E"
#define CHARACTERISTIC_UUID_TX "6E400003-B5A3-F393-E0A9-E50E24DCCA9E"

// Configuration UART pour le GNSS
#define RX_PIN D7
#define TX_PIN D6

// Buffer RTCM avec paramètres stables
#define RTCM_BUFFER_SIZE 1536
uint8_t rtcmBuffer[RTCM_BUFFER_SIZE];
int rtcmBufferHead = 0;
int rtcmBufferTail = 0;
unsigned long lastRtcmWrite = 0;

// Paramètres fixes optimisés
const unsigned long RTCM_WRITE_INTERVAL = 1;
const int RTCM_BYTES_PER_WRITE = 80;

// Gestion reconnexion
BLECharacteristic *pCharacteristicTX;
BLEServer *pServer;
bool deviceConnected = false;
bool wasConnected = false;
unsigned long disconnectionTime = 0;
const unsigned long RECONNECT_DELAY = 500;

String nmeaBuffer;

// Fonctions buffer RTCM (inchangées)
void addToRtcmBuffer(const uint8_t* data, size_t len) {
  for (size_t i = 0; i < len; i++) {
    int nextHead = (rtcmBufferHead + 1) % RTCM_BUFFER_SIZE;
    if (nextHead != rtcmBufferTail) {
      rtcmBuffer[rtcmBufferHead] = data[i];
      rtcmBufferHead = nextHead;
    } else {
      rtcmBufferTail = (rtcmBufferTail + 1) % RTCM_BUFFER_SIZE;
      rtcmBuffer[rtcmBufferHead] = data[i];
      rtcmBufferHead = nextHead;
    }
  }
}

int readFromRtcmBuffer(uint8_t* data, int maxLen) {
  int count = 0;
  while (rtcmBufferTail != rtcmBufferHead && count < maxLen) {
    data[count++] = rtcmBuffer[rtcmBufferTail];
    rtcmBufferTail = (rtcmBufferTail + 1) % RTCM_BUFFER_SIZE;
  }
  return count;
}

int getBufferLevel() {
  return (rtcmBufferHead - rtcmBufferTail + RTCM_BUFFER_SIZE) % RTCM_BUFFER_SIZE;
}

// Callbacks BLE — signature simple sans esp_ble_gatts_cb_param_t
class MyServerCallbacks : public BLEServerCallbacks {
  void onConnect(BLEServer* pServer) {
    deviceConnected = true;
    wasConnected = true;
    // iOS négocie automatiquement les paramètres de connexion BLE
  };

  void onDisconnect(BLEServer* pServer) {
    deviceConnected = false;
    disconnectionTime = millis();
    // Le watchdog dans loop() gère le re-advertising avec délai
  }
};

class MyCallbacks : public BLECharacteristicCallbacks {
  void onWrite(BLECharacteristic *pCharacteristic) {
    String rxValue = pCharacteristic->getValue();
    if (rxValue.length() > 0) {
      addToRtcmBuffer((const uint8_t*)rxValue.c_str(), rxValue.length());
    }
  }
};

void setup() {
  Serial.begin(115200);
  Serial1.begin(115200, SERIAL_8N1, RX_PIN, TX_PIN);

  BLEDevice::init("Blue_RTK_01");
  BLEDevice::setMTU(512);

  pServer = BLEDevice::createServer();
  pServer->setCallbacks(new MyServerCallbacks());

  BLEService *pService = pServer->createService(SERVICE_UUID);

  pCharacteristicTX = pService->createCharacteristic(
                      CHARACTERISTIC_UUID_TX,
                      BLECharacteristic::PROPERTY_NOTIFY
                    );
  pCharacteristicTX->addDescriptor(new BLE2902());

  BLECharacteristic *pCharacteristicRX = pService->createCharacteristic(
                                         CHARACTERISTIC_UUID_RX,
                                         BLECharacteristic::PROPERTY_WRITE
                                       );
  pCharacteristicRX->setCallbacks(new MyCallbacks());

  pService->start();

  BLEAdvertising *pAdvertising = BLEDevice::getAdvertising();
  pAdvertising->addServiceUUID(SERVICE_UUID);
  pAdvertising->setScanResponse(true);
  pAdvertising->setMinPreferred(0x06);
  pAdvertising->setMinPreferred(0x12);
  BLEDevice::startAdvertising();
}

void loop() {
  // Watchdog reconnexion BLE avec délai
  if (!deviceConnected && wasConnected) {
    if ((millis() - disconnectionTime) >= RECONNECT_DELAY) {
      wasConnected = false;
      BLEDevice::startAdvertising();
    }
  }

  // Gestion RTCM paramètres fixes
  if ((millis() - lastRtcmWrite) >= RTCM_WRITE_INTERVAL) {
    int bufferLevel = getBufferLevel();
    if (bufferLevel > 0) {
      uint8_t rtcmData[120];
      int bytesToRead = min(bufferLevel, RTCM_BYTES_PER_WRITE);
      int bytesRead = readFromRtcmBuffer(rtcmData, bytesToRead);
      if (bytesRead > 0) {
        Serial1.write(rtcmData, bytesRead);
        Serial1.flush();
      }
    }
    lastRtcmWrite = millis();
  }

  // Lecture NMEA du GNSS
  while (Serial1.available()) {
    char c = Serial1.read();
    if (c == '\n') {
      if (deviceConnected && nmeaBuffer.length() > 0) {
        String trameAEnvoyer = nmeaBuffer;
        if (!trameAEnvoyer.endsWith("\r")) trameAEnvoyer += "\r\n";
        pCharacteristicTX->setValue(trameAEnvoyer.c_str());
        pCharacteristicTX->notify();
        nmeaBuffer = "";
      }
    }
    else if (c != '\r') {
      nmeaBuffer += c;
    }
  }

  delay(1);
}

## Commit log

2024-12-07 Create Schema_GNSS-RTK.jpg
    Add wiring schéma
2024-12-07 Add 3D printing files
    Add stl files for 3D print
    [Boitier gnss RTK 16.stl, Capot gnss RTK 15D.stl, Capot gnss RTK 15G.stl]
2025-06-29 Add program for ESP32C3
    Arduino program for BLE with XIAO ESP32C3
2025-08-30 New ESP32C3 version and 3D print
    New ESP32C3 version and 3D print, part list for the ZED-X20P
    [Boitier gnss RTK 16.stl, Boitier-slim-V9.stl, Capot gnss RTK 15D.stl, Capot gnss RTK 15G.stl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]
2025-09-20 Updated wiring schéma
2026-03-03 Nouveau boitier a imprimer
    Version du boitier pour un PCB qui remplace le cablage
    [Boitier-slim-V10-PCB.stl, Boitier-slim-V9.stl, Capot-slim-V9.stl]
2026-04-06 Add STP files
    Add STP version for 3D printing
    [Boitier-avec-PCB.stp, Capot-avec-PCB.stp]
2026-05-31 Adding PCB and new 3D print files
    Adding files for PCB board and new 3D print files to include PCB board
    [Boitier-avec-PCB.stp, Boitier-slim-V10-PCB.stl, Boitier_RTK - Fond.step, Boitier_RTK - Fond.stl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]
2026-06-06 Update README.md
    Update readme for the new PCB project
